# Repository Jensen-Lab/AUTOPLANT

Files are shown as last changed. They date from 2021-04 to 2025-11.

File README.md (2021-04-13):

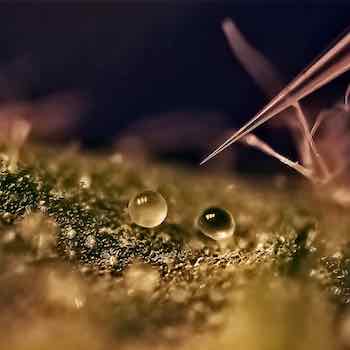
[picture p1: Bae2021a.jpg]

# Supplemental Online Material
Neural networks and robotic microneedles enable autonomous extraction of plant metabolites

Plant Physiology (2021)

Hansol Bae, Magnus Paludan, Jan Knoblauch and Kaare H. Jensen

Department of Physics, Technical University of Denmark, DK-2800 Kgs. Lyngby

E-mail for correspondence: khjensen@fysik.dtu.dk

This repository contains scripts for
1. controlling a Sutter Instruments ROE-200 micromanipulator ("micromanipulator/") 
2. generating training data for a CNN for glandular trichome detection on micrographs ("generate_training_data/") 
3. training (transfer learning) GoogLeNet for glandular trichome detection on micrographs ("train_neural_network/") 
4. testing the network on micrographs ("test_neural_network/") 

To generate training data, train the network, and test the network follow these steps: 
Steps 1-4 may be skipped, as the network is already trained (network weights in train_neural_network/neuralNet.mat). 

Generating training data (MAY BE SKIPPED): 
1. make folder "training_data" in "generate_training_data". 
2. make folders "negative" and "positive" in "generate_training_data/training_data" 
3. run the MATLAB code "generate_training_data/generate_training_data.m"

Training (transfer learning) GoogLeNet CNN (MAY BE SKIPPED): 
4. run the MATLAB code "train_neural_network/train_network.m" 

Test the neural network: 
5. run the MATLAB code test_neural_network/test_network.m 
6. on line 16 the variable "imageNo" may be changed to any image index in "generate_training_data/full_res_images/". Alternatively, a full-path to a micrograph may be inserted in line 17.

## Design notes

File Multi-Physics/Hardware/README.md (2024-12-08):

# Six-Axis Micro Manipulator Assembly Guide

## Overview
This document provides detailed instructions for assembling the Six-Axis Micro Manipulator.

## Hardware Requirements
A list of all required hardware is provided in the file `Parts.xlsx` including links to suppliers for purchase of commercial available parts. 
- Parts marked as 'bought' will have to be purchased.
- Parts marked as '3D Print' will have to be 3D printed. The corresponding `.stl` files can be found in the folder `3DPrints` sorted into the individual axis.
- Parts that are marked as `Workshop` are metal components. Files with dimensions are included in `Metal_Connectors`. These parts will have to be made or ordered.

### Additional Requirements
- Screws (M2, M3, M4 and M6 of adequate lengths)
- Screwdrivers (corresponding to the screws)

## Electronics Required
The wiring digrams (Schematics) for the electronic setup is included in the folder `PCB`.
- Schematic for the motor drivers. If all six axis are in use, this electronis set-up has to be repeated for each individual axis (For ordering a premade PCB: Gerber, BOM and Pick and Place Files are available for a manual control of the motor (see `software`for the difference in manual and automatic control)
- Schematic for the electronic setup of the `electrode` probe.
- Schematic for the electronis setup of the `laser`probe.

### Additional Requirements
- Wire extensions / Connetions
- Breadboards
- (Soldering Iron)

## Assembly Instructions
The `3DPrints/Robot.step` file illustrates how the different parts fit together. Remember to wire the motors according to the elctronic schematics after assembly.

If automatic mode is wished (as of now implemented only for x,y, and r), follow these steps:
- glue the magnet holder to the back of the motor (the free rotating piece)
- add the magnet
- add the sensor board on the shield
- attach the motorscrew spacer and then the sensor shield to the back of the motor (screws of the motor have to be exchanged for longer ones)
- add the wiring

### Step 1: Z-Axis
- The axis is the base. Add the brackets at the desired height and attach the platform.
- The motor is connected via the metal connector and kept in place with the clamp, plate and block.

### Step 2: Rotational-Axis 1
- A base plate for extra height is the base.
- Attach the Stage to this platform in such a way that the connection to the motor will cross over the flat corner.
- Attach the base to the Z-axis.
- Add the motor via the metal connector. It is held in place at the appropiate distance on the Z axis with the printed motor holder

### Step 3: X-Axis and Y-Axis
- For extra height place the height plate in between the rotational 1 axis and the x axis.
- Attach the motors to the motor holders (x and y).
- Attach the moving part of the x stage (bottom) to the y holder
- Attach the x stage to the X-Stage print (on the non movable part)
- Now the printed stages x and y should be just on top of each other.
- Connect the motor holder and the x stage print with the connection piece and connect the motor shaft with the x axis via the metal connection.
- Connect the y stage onto the movable part of the x stage
- Connect the y axis with the motor shaft via the metal connector.
- Connect the stage system to rotation 1.

### Step 4: Rotational Axis 2
- Attach the motor holder to the y stage
- Add the motor to the holder (be careful when exchanhing the screws of the motor for attachment, so the gears do not fall out of the box.

### Step 5: R-Axis
- Add the motor to the holder
- Add the stage to the holder and connect the stage and motor via the metal connector.
- Add the metal rod to the rod holder and attach the piece to the stage
- Attach the stage to the rotatonal axis 2

## Connection with the PC
For setting up the software see the `README.md` file in the `Software` folder

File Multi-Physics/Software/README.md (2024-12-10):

# Six-Axis Micro Manipulator Control

## Overview
This web application provides an interface to control a six-axis movement system integrated with camera functionalities (Basler acA1920-150uc), acquisition settings, and end effector controls. The app allows users to manipulate and monitor their equipment through a web interface.

## Features
- **Six-Axis Movement Control**: Control over all six axis.
- **Camera Integration**: Live camera view to monitor operations.
- **Acquisition Settings**: Customizable settings to adjust the camera acquisition parameters.
- **End Effector Control**: Interface to access the Laser and Electrode probes.

## Requirements
- Compatible with Linux systems.
- Requires Python 3.8 or newer.
- Dependencies are listed in the `requirements.txt` file.
- Requires the six axis micromanipulator as designed here

## Folders
- **Micromanipulator App**: Here the user interface is designed.
- **Stepper Motor Code**: This code should be uploaded to the microcontrollers (`Raspberry Pi Picos`) of the stepper motors. It defines all necessary movement control, use eg `PlatformIO Core` for uploading the code
- **Electrode**: This code should be uploaded to the microcontroller (`Arduino Nano`) of the Electrode to allow for control of the switch, use eg `PlatformIO Core` for uploading the code.
- **Laser**: This code should be uploaded to the microcontroller (`Arduino Nano`) of the Laser to allow for control of the switch, use eg `PlatformIO Core` for uploading the code.

## Installation
To set up the web app on your local system, follow these steps:
1. Clone the repository to your local machine.
2. Navigate to the cloned directory.
3. Install the required Python dependencies:
   ```bash
   pip install -r requirements.txt
4. Inside of `Micromanipulator App/website/view.py` change the following:
   - `path`: change to the path that should be used to save images and videos
   - `SN_dict`: change to the serial numbers of the respective used microcontrollers

## Use
To open the web application, follow these steps:
1. Navigate to the directory containing `main.py` (in `Micromanipulator App/`)
2. run
    ```bash
   python main.py
4. Access the web app through your browser at the specified local address

### Camera
1. Turn on the camera (`Real-Time Display Basler`) -  Make sure the camera is connected via USB
2. Change exposure, gain blacklevel and gamma value accordingly (`Camera Settings`)
3. Change the total time of a video to be taken and the fps value (`Video Acquisition Settings`)
4. Take an image or video

### Axes
- Connect an axis and wait for the green symbol to appear next to the axis name (`Connection`)
- Input the number of steps in `manual` mode in `Robot Control` to move that amount; in `automatic` mode input the positional change
    (Note: in `automatic` mode a magnet is used to control the positioning)
    (Note: The tick box next to some axes in `Robot Control` changes the movement mode from `manual` to `automatic` when ticked)
- Movement the axis with the corresponding arrows (`Robot Control`)
  
### Electrode 
`Electroshocker Settings`
- Change the total on time of the electrode (eg 60s)
- Change the time the electrode is on (eg 1s)
- Change the time the electrode is off (eg 10s)

### Laser
`Laser Settings`
- Change the total on time of the laser (eg 60s)
- Change the time the laser is on (eg 1s)
- Change the time the laser is off (eg 10s)

## Liscence

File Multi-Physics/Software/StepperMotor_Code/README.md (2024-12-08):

How to build PlatformIO based project
=====================================

1. [Install PlatformIO Core](https://docs.platformio.org/page/core.html)
2. Download [development platform with examples](https://github.com/platformio/platform-raspberrypi/archive/develop.zip)
3. Extract ZIP archive
4. Run these commands:

```shell
# Change directory to example
$ cd platform-raspberrypi/examples/arduino-blink

# Build project
$ pio run

# Upload firmware
$ pio run --target upload

# Clean build files
$ pio run --target clean
```

## Notes

For Raspberry Pi Pico devices, two Arduino cores exist:
* https://github.com/arduino/ArduinoCore-mbed
* https://github.com/earlephilhower/arduino-pico

This examples showcases how to use both of these cores in the `platformio.ini`.

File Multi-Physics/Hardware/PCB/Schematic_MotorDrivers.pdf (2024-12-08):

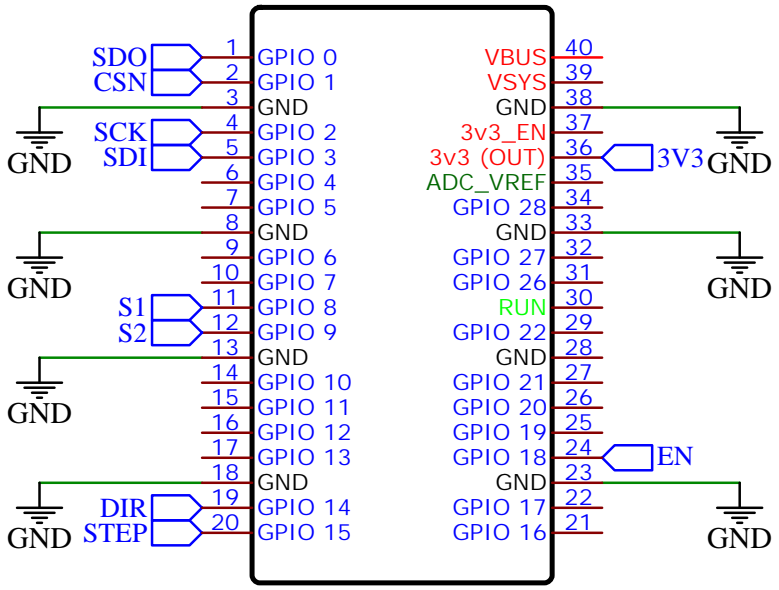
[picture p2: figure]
GND; STEP; DIR; SDI; SCK; CSN; SDO; GPIO 0 1; GPIO 1; GPIO 2; GPIO 3; GPIO 4; GPIO 5; GPIO 6; 9 GPIO 7 10 GPIO 8 11 GPIO 9 12 GND 13 GPIO 10 14 GPIO 11 15 GPIO 12 16 GPIO 13 17 GND 18 GPIO 14 19

GPIO 15 20 | GPIO 16 21 GPIO 17 22 GND 23 GPIO 18 24 GPIO 19 25 GPIO 20 26 GPIO 21 27 GND 28 GPIO 22 29 RUN 30 GPIO 26 31 GPIO 27 32 GND 33 GPIO 28 34 ADC_VREF 35 3v3 (OUT) 36 3v3_EN 37 GND 38 VSYS 39 VBUS 40

## Raspberry Pi Pico

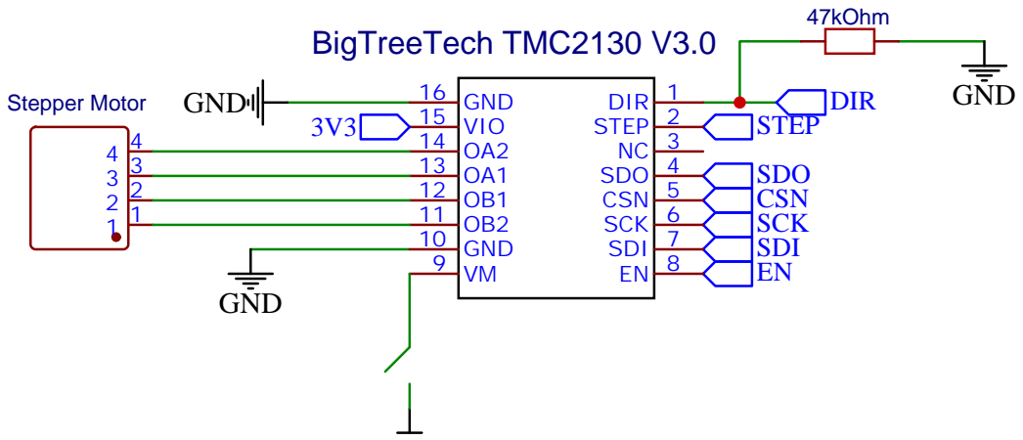
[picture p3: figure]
GND; 47kOhm; DIR; SDI; SCK; CSN; SDO; STEP; BigTreeTech TMC2130 V3.0; Stepper Motor 1 1 2 2 3 3 4 4

GND 10 OB2 11 OB1 12 OA1 13 OA2 14 VIO 15 GND 16

12V

## AS5048B-AB-1.1

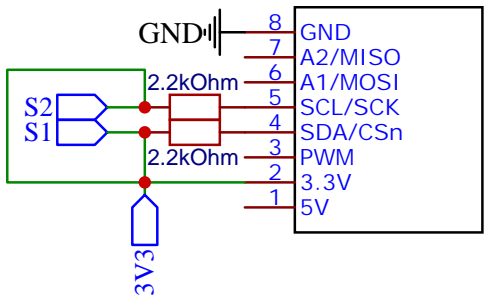
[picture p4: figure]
PWM; SDA/CSn; SCL/SCK; A1/MOSI; A2/MISO; GND; 8 GND; 2.2kOhm

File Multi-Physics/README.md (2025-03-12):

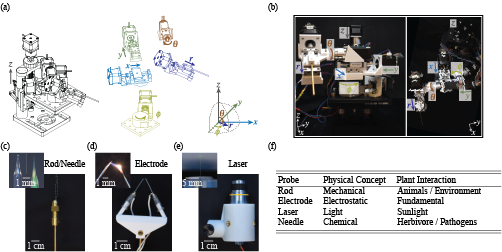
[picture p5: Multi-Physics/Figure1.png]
Key Figure


# Supplemental Material for "A multi-physics approach to probing plant responses: From calcium signaling to thigmonastic motion"

This repository contains supplemental material for the paper titled:

"A multi-physics approach to probing plant responses: From calcium signaling to thigmonastic motion" 
Sabrina Gennis, Matthew D. Biviano, Kristoffer P. Lyngbirk, Hannah R. Thomas, Viktoriya Vasina, Christine Faulkner, Michael Knoblauch and Kaare H. Jensen

Here, you will find additional data, and resources to build and use the six axis micromanipulator and the different probes that are used in the paper.

## Contact Information
**Kaare Jensen**
- Email: khjensen@fysik.dtu.dk
- Institution: Department of Physics, Technical University of Denmark, DK-2800 Kgs. Lyngby

## Contents of This Repository
- `Hardware/`: Description of all the hardware needed for building the system and instructions for setting it up.
- `Software/`: Directory containing the software for the system.

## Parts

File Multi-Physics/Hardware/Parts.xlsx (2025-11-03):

Micromanipulator
Parts and Costs
Movement Axis | Part | 3DPrint | Workshop | Bought | Order Number | Cost | Quantity | Total Cost in EUR | Conversion Rate
X-Axis | Stage |  |  | norelem | 21134-304 (https://www.norelem.com/dk/en/Products/Product-overview/Systems-and-components-for-machine-and-plant-construction/21000-Slides-Guide-rails-Positioning-tables-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) | 275.54 € | 1 | 275.54 € | USD to EUR | 0.89
 | Motor |  |  | makersupplies | MT-1703HSM168A (https://makersupplies.dk/electrical-cnc-electronics/stepper-drivers-motors/hybrid-stepper-motor/stepper-drivers-motors-stepper-motors-hybrid-stepper-motor-mot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) | 212.50 kr. | 1 | 28.48 € | DKK to EUR | 0.134
 | X-axis - MotorHolderNema17 | PLA |  |  |  |  | 1
 | X-axis - Height_Plate | PLA |  |  |  |  | 1
 | X-axis - X_stage_on_rotational_stage | PETG |  |  |  |  | 1
 | X-axis - Connection | PETG |  |  |  |  | 1
 | Stages_Drive connector |  | Metall |  |  |  | 1
 | Megnetic Sensor Board |  |  | RS | 201-8314 (https://dk.rs-online.com/web/p/sensor-udvikling/2018314?searchId=9923297d-1d02-4ba0-9d2d-780a1fe3a02a) | 130.60 kr. | 1 | 17.50 €
 | Motor_sensor_shield | PLA |  |  |  |  | 1
 | Motor-magnet-holder | PLA |  |  |  |  | 1
 | motorscrew-spacer | PLA |  |  |  |  | 1
Y-Axis | Stage |  |  | norelem | 21120-04 (https://www.norelem.com/dk/en/Products/Product-overview/Systems-and-components-for-machine-and-plant-construction/21000-Slides-Guide-rails-Positioning-tables-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) | 241.44 € | 1 | 241.44 €
 | Motor |  |  | makersupplies | MT-1703HSM168A (https://makersupplies.dk/electrical-cnc-electronics/stepper-drivers-motors/hybrid-stepper-motor/stepper-drivers-motors-stepper-motors-hybrid-stepper-motor-mot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) | 212.50 kr. | 1 | 28.48 €
 | Y-axis - Holder | PLA |  |  |  |  | 1
 | Stages_Drive connector |  | Metall |  |  |  | 1
 | Megnetic Sensor Board |  |  | RS | 201-8314 (https://dk.rs-online.com/web/p/sensor-udvikling/2018314?searchId=9923297d-1d02-4ba0-9d2d-780a1fe3a02a) | 130.60 kr. | 1 | 130.60 €
 | Motor_sensor_shield | PLA |  |  |  |  | 1
 | Motor-magnet-holder | PLA |  |  |  |  | 1
 | motorscrew-spacer | PLA |  |  |  |  | 1
Z-Axis | Stage |  |  | thorlabs | VAP4/M (https://www.thorlabs.com/newgrouppage9.cfm?objectgroup_id=9434) | $812.53 | 1 | 723.15 €
 | Motor |  |  | amazon | Stepperonline 27:1 Planetary Gear Nema 17 (https://www.amazon.de/dp/B077YXYTDD?psc=1&ref=ppx_yo2ov_dt_b_product_details) | 45.16 € | 1 | 45.16 €
 | Z-axis_Motor connector |  | Metall |  |  |  | 1
 | Z-axis_Motor clamp | PLA |  |  |  |  | 1
 | Z-axis_Motor plate | PLA |  |  |  |  | 1
 | Z-axis_Mount block | PLA |  |  |  |  | 1
 | Platform |  |  | thorlabs | MB1515/M (https://www.thorlabs.com/thorproduct.cfm?partnumber=MB1515/M) | $57.07 | 1 | 50.79 €
 | Platform Brackets |  |  | thorlabs | AB90A/M (https://www.thorlabs.com/thorproduct.cfm?partnumber=AB90A/M) | $30.58 | 2 | $54.43
Rotational Axis | Stage |  |  | norelem | 21160-08 (https://www.norelem.com/dk/en/Products/Product-overview/Systems-and-components-for-machine-and-plant-construction/21000-Slides-Guide-rails-Positioning-tables-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) | 344.38 € | 1 | 344.38 €
 | Motor |  |  | amazon | Stepperonline 27:1 Planetary Gear Nema 17 (https://www.amazon.de/dp/B077YXYTDD?psc=1&ref=ppx_yo2ov_dt_b_product_details) | 45.16 € | 1 | 45.16 €
 | Rot-axis - MotorHolderNema17 | PETG |  |  |  |  | 1
 | Stages_Drive connector |  | Metall |  |  |  | 1
 | Rot-axis - BasePlate | PLA |  |  |  |  | 1
Rotational 2 Axis | Motor |  |  | amazon | Stepperonline 14:1 Planetary Gear Nema 11 (https://www.amazon.de/-/en/dp/B077Z7WGV6?ref=ppx_yo2ov_dt_b_fed_asin_title) | 212.50 kr. | 1 | 50.00 €
 | Rot2_MotorHolderNema11 | PLA |  |  |  |  | 1
R-axis | Motor |  |  | amazon | Stepperonline Nema 11 Geared Motor 14:1 Planetary Gearbox 0.67A Stepper Motor (https://www.amazon.de/dp/B077Z7WGV6?ref=ppx_yo2ov_dt_b_fed_asin_title) | 114.27 € | 1 | 114.27 €
 | r-axis_holder | PETG |  |  |  |  | 1
 | r-axis_rod_holder | PLA |  |  |  |  | 1
 | Stages_Drive connector |  | Metall |  |  |  | 1
 | Metal Rod (3mm diameter) |  | Metall |  |  |  | 1
 | Megnetic Sensor Board |  |  | RS | 201-8314 (https://dk.rs-online.com/web/p/sensor-udvikling/2018314?searchId=9923297d-1d02-4ba0-9d2d-780a1fe3a02a) | 130.60 kr. | 1 | 17.50 €
 | Motor_sensor_shield | PLA |  |  |  |  | 1
 | Motor-magnet-holder | PLA |  |  |  |  | 1
 | motorscrew-spacer | PLA |  |  |  |  | 1
Power Supply | Power Supply 24V |  |  | amazon | IRM-60-24ST AC/DC 60W (https://www.amazon.de/gp/product/B01H0X8EJI/ref=ppx_yo_dt_b_asin_title_o02_s00?ie=UTF8&psc=1) | 21.00 € | 1 | 21.00 €
 | Power Supply Box |  |  | amazon | ABS Housing 158x90x60 (https://www.amazon.de/gp/product/B0747M7BWZ/ref=ppx_yo_dt_b_asin_title_o01_s02?ie=UTF8&th=1) | 13.23 € | 1 | 13.23 €
 | PCB Power Divider |  |  | JLCPCB | own design | 5.05 € | 1 | 5.05 €
 | Power Divider Box |  |  | amazon | ABS Housing 158x90x60 (https://www.amazon.de/gp/product/B0747M7BWZ/ref=ppx_yo_dt_b_asin_title_o01_s02?ie=UTF8&th=1) | 13.23 € | 1 | 13.23 €
 | Stop Button |  |  | amazon | Emergency Stop Switch 12-220V 3A 1NO 1NC (https://www.amazon.de/gp/product/B07S2VJT9Q/ref=ppx_yo_dt_b_asin_title_o07_s01?ie=UTF8&th=1) | 15.75 € | 1 | 15.75 €
Driver Electronics | Motor Drivers |  |  | amazon | TMC2130 V3.0 SPI 4x (https://www.amazon.de/gp/product/B07RQXZCGX/ref=ppx_yo_dt_b_asin_title_o07_s01?ie=UTF8&psc=1) | 37.80 € | 2 | 75.60 €
 | Raspberry Pi Pico |  |  | digikey | 2648-SC0915CT-ND (https://www.digikey.com/en/products/detail/raspberry-pi/SC0915/13624793) | $4.00 | 6 | 21.36 €
 | PCB Boards Drivers |  |  | JLCPCB | own design | 2.50 € | 6 | 15.00 €
 | Switches |  |  | amazon | Toggle Switch 10x (https://www.amazon.de/gp/product/B083NLCDQG/ref=ppx_yo_dt_b_asin_title_o00_s00?ie=UTF8&th=1) | 9.44 € | 1 | 9.44 €
 | Electronics Box |  |  | RS | 2010206 (https://de.rs-online.com/web/p/universalgehause/2010206?searchId=89035b39-1f88-4bc5-9d30-509afda7214d&gb=s) | 53.53 € | 1 | 53.53 €
Generel | Nuts and Bolts
 | Brass inserts |  |  | amazon | 330 pieces threaded insert nut (https://www.amazon.de/gp/product/B082R28J4T/ref=ppx_yo_dt_b_asin_title_o06_s00?ie=UTF8&psc=1) | 14.70 € | 1 | 14.70 €
 | USBA-Micro Cable |  |  | RS | 2527125 5x (https://de.rs-online.com/web/p/usb-kabel/2527125?searchId=ae20c1eb-bfac-4bae-ba3b-54ca0c1161e8&gb=s) | 10.57 € | 2 | 21.14 €
 | USBA-USBA Cable |  |  | RS | 2513218 5x (https://de.rs-online.com/web/p/usb-kabel/2513218?searchId=9832e634-1913-4e33-acd7-2c80567f8a2b&gb=s) | 9.77 € | 2 | 19.54 €
Camera | Basler Camera |  |  | Basler | Basler acA1920-150uc (https://www.baslerweb.com/en/shop/aca1920-150uc/) | $1000.00 | 1 | 890.00 €
 |  |  |  |  |  |  |  | 3355.45 €
Probes
Rod | Holder | PETG |  | amazon | Mesee 3 Sets 0.5-3mm Brass Drill Chuck (https://www.amazon.com/dp/B08XWWZ41R?smid=A38WK9AYQDX0WE&ref_=chk_typ_imgToDp&th=1) | $7.99 | 1 | 7.11 €
Electrode | holder | PETG
 | electrical recharchable lighter |  |  | coop
 | arduino nano |  |  | RS | 1927586 (https://de.rs-online.com/web/p/arduino/1927586?searchId=250e394d-1db6-4d03-8f04-e056930f3700&gb=s) | 13.03 € | 1 | 13.03 €
 | relay |  |  | amazon | Electrely 6pcs 1 Channel Relay Module, 5V (https://www.amazon.de/dp/B07GRW83FR?ref=ppx_yo2ov_dt_b_fed_asin_title) | 9.44 € | 1 | 12.48 €
Laser | laser pointer green |  |  | amazon | CTRICALVER 1 x 520 nm 5.5-6 V green laser (https://www.amazon.de/gp/product/B08QYNZDD4/ref=ppx_yo_dt_b_asin_title_o03_s01?ie=UTF8&th=1) | 13.23 € | 1 | 13.23 €
 | microscope lens |  |  | amazon | 10x 185 achromatic lens (160/0.17) (https://www.amazon.de/gp/product/B07PPGDVQK/ref=ppx_yo_dt_b_asin_title_o00_s03?ie=UTF8&psc=1) | 18.98 € | 1 | 18.98 €
 | holder | PETG |  |  |  |  |  | 0.00 €
 | arduino nano |  |  | RS | 1927586 (https://de.rs-online.com/web/p/arduino/1927586?searchId=250e394d-1db6-4d03-8f04-e056930f3700&gb=s) | 13.03 € | 1 | 13.03 €
 | relay |  |  | amazon | Electrely 6pcs 1 Channel Relay Module, 5V (https://www.amazon.de/dp/B07GRW83FR?ref=ppx_yo2ov_dt_b_fed_asin_title) | 9.44 € | 1 | 12.48 €
 |  |  |  |  |  |  |  | 90.34 €

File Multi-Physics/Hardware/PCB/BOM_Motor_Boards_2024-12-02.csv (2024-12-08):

ID | Name | Designator | Footprint | Quantity | Manufacturer Part | Manufacturer | Supplier | Supplier Part | Price
1 | WJ126V-5.0-2P | P2 | CONN-TH_WJ126V-5.0-2P | 1 | WJ126V-5.0-2P | KANGNEX(康奈克斯电气) | LCSC | C8404 | 0.068
2 | X5511FV-20-C30D97-0970 | U3,U4 | HDR-TH_20P-P2.54-V-F-4 | 2 | X5511FV-20-C30D97-0970 | XKB Connectivity(中国星坤) | LCSC | C2883486 | 0.707
3 | 912-112A1027D10100 | USB2 | USB-A-TH_912-112A1027D10100 | 1 | 912-112A1027D10100 | 精拓金 | LCSC | C2763281 | 0.129
4 | 47kΩ | R1 | R0402 | 1 | ERA2AEB473X | PANASONIC(松下) | LCSC | C543615 | 0.12
5 | XH-4AW M | CN1 | CONN-TH_XH2.54-4AW | 1 | - | Boom Precision Elec | LCSC | C146115 | 0.021
6 | X6511FV-08-C85D32 | H3,H4 | HDR-TH_8P-P2.54-V-F | 2 | X6511FV-08-C85D32 | XKB Connectivity(中国星坤) | LCSC | C718237 | 0.192

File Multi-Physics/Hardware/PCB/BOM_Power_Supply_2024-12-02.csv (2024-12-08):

ID | Name | Designator | Footprint | Quantity | Manufacturer Part | Manufacturer | Supplier | Supplier Part | Price
1 | WJ126V-5.0-2P | P2,P1 | CONN-TH_WJ126V-5.0-2P | 2 | WJ126V-5.0-2P | KANGNEX(康奈克斯电气) | LCSC | C8404 | 0.068
2 | 100uF | C1 | CAP-SMD_BD6.3-L6.6-W6.6-LS7.3-FD | 1 | GVZ1H101M0607 | HONOR(荣誉) | LCSC | C2980173 | 0.067
3 | 1N4007_C211605 | D1 | DO-41_BD2.4-L4.7-P8.70-D0.9-FD | 1 | 1N4007 | YANGJIE(扬杰) | LCSC | C211605 | 0.034
4 | 912-112A1027D10100 | USB1,USB2,USB3,USB4,USB5,USB6 | USB-A-TH_912-112A1027D10100 | 6 | 912-112A1027D10100 | 精拓金 | LCSC | C2763281 | 0.129
5 | 220kΩ | R3 | RES-TH_BD2.3-L6.5-P10.50-D0.5 | 1 | RI40-1/4W-220KΩ ±1% T | CCO(千志电子) | LCSC | C136543 | 0.064

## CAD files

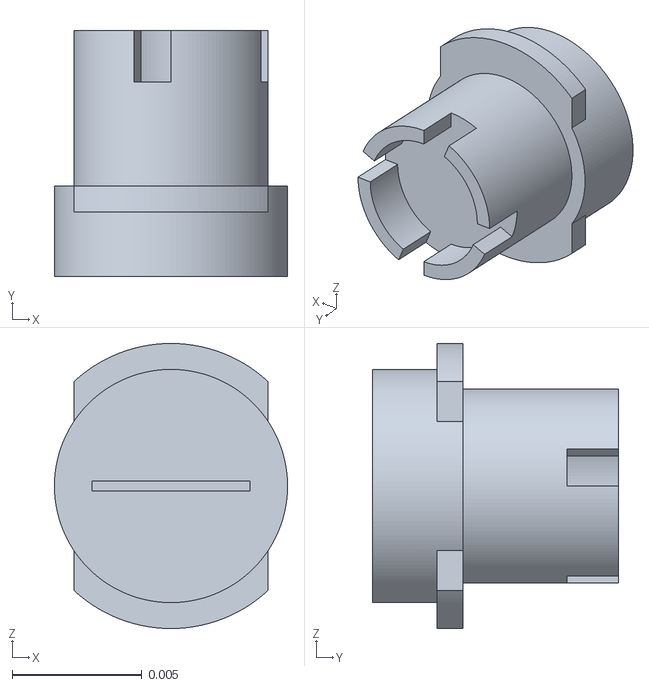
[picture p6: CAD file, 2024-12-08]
Multi-Physics/Hardware/3DPrints/Position_Sensor/Motor-magnet-holder.stl
0.009 x 0.0095 x 0.011

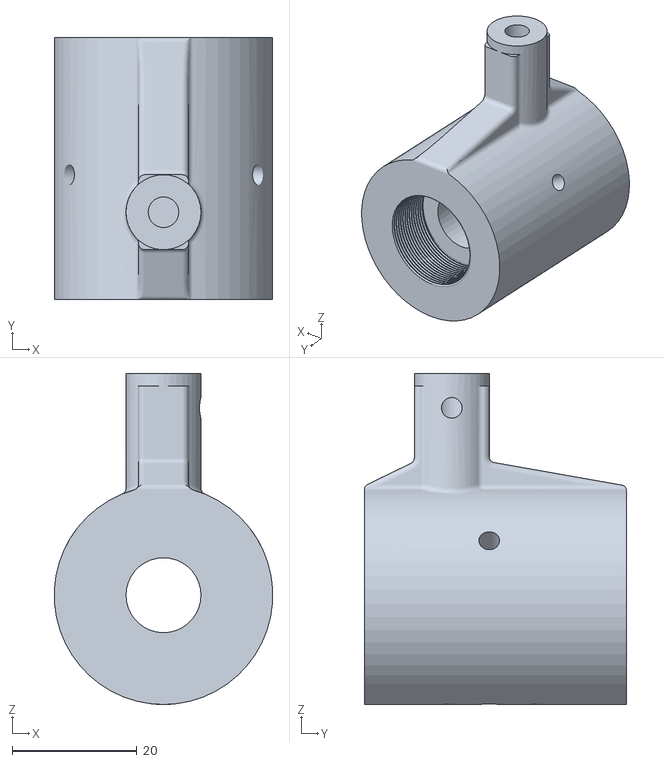
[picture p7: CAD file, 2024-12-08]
Multi-Physics/Hardware/3DPrints/Probes/Laser_Holder.stl
35.0 x 42.0 x 53.0

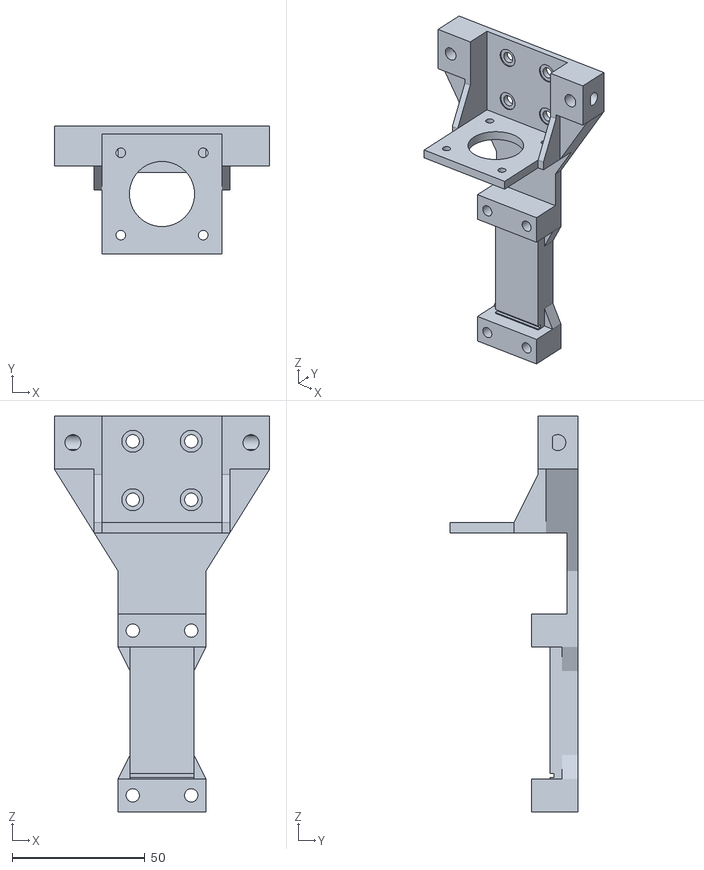
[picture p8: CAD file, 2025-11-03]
Multi-Physics/Hardware/3DPrints/r-axis/r-axis_holder.stl
81.0 x 48.0 x 149.0

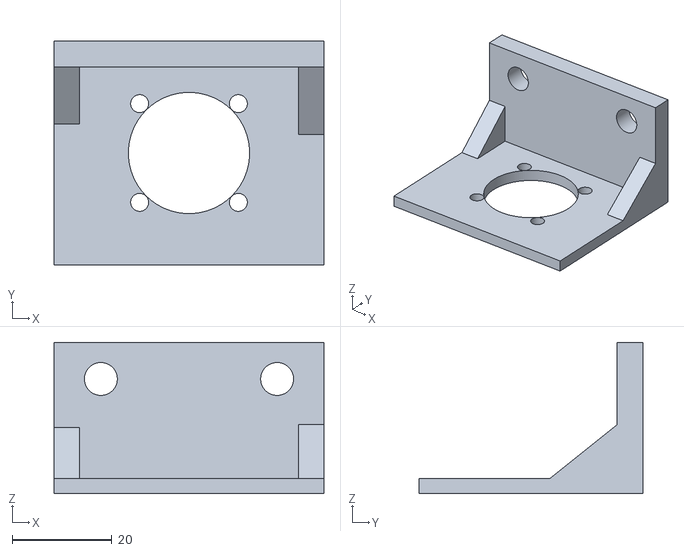
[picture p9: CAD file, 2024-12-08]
Multi-Physics/Hardware/3DPrints/Rot1-axis/Rot-axis - MotorHolderNema17.stl
54.2 x 45.0 x 30.3

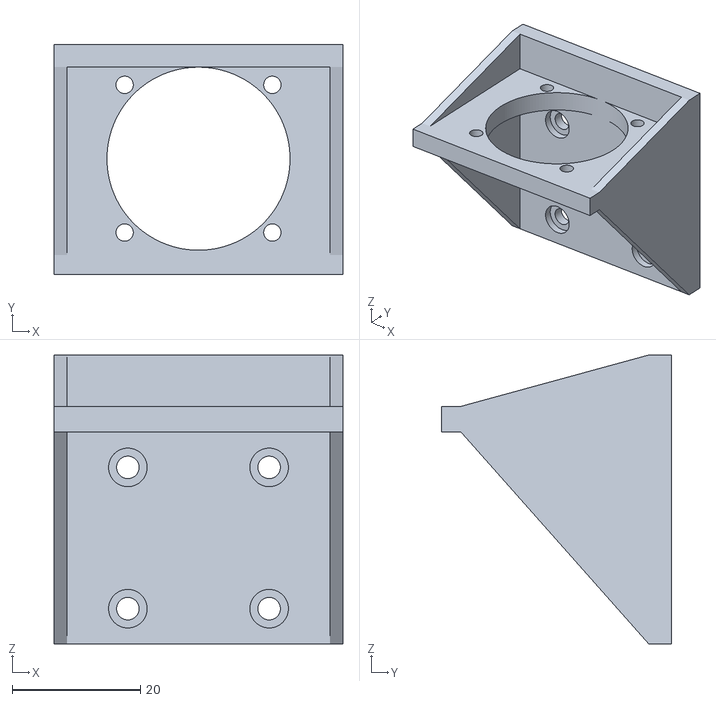
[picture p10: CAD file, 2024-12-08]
Multi-Physics/Hardware/3DPrints/Rot2-axis/Rot2_MotorHolderNema11.stl
45.0 x 35.8 x 45.0

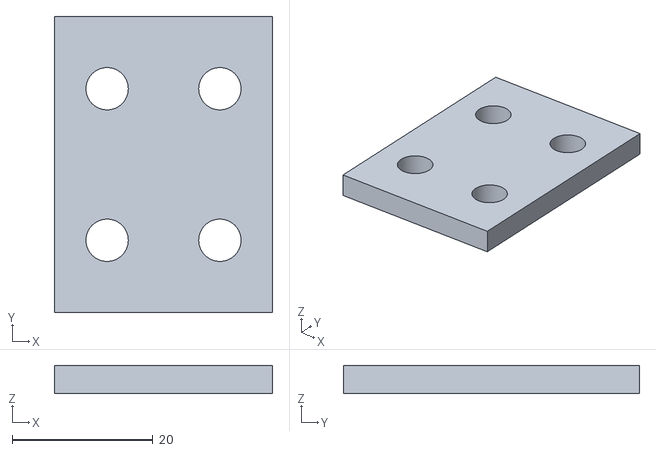
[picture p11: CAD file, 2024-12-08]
Multi-Physics/Hardware/3DPrints/X-axis/X-axis - Connection.stl
31.0 x 42.0 x 4.00

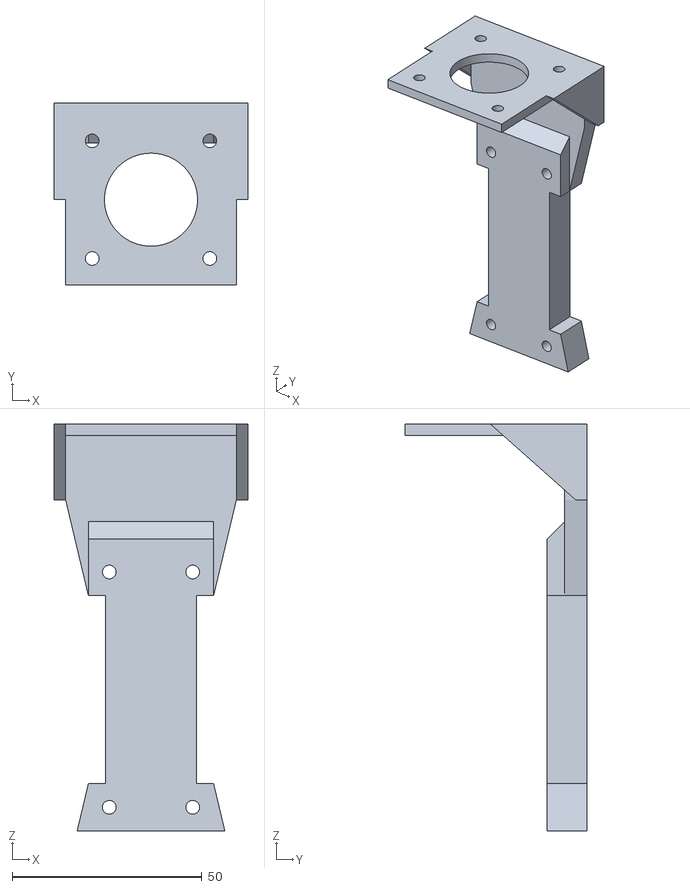
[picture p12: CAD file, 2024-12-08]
Multi-Physics/Hardware/3DPrints/Y-axis/Y-axis - Holder.stl
51.0 x 48.0 x 107.2

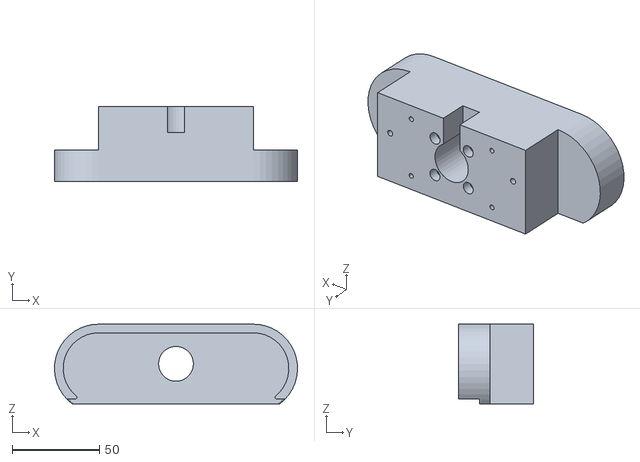
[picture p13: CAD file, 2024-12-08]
Multi-Physics/Hardware/3DPrints/Z-axis/Z-axis_Mount block.STL
139.5 x 43.2 x 45.8

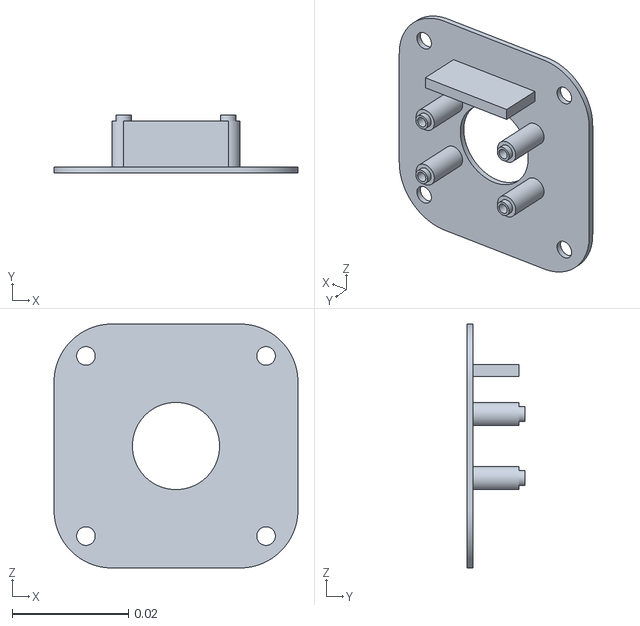
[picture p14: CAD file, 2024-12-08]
Multi-Physics/Hardware/3DPrints/Position_Sensor/Motor_sensor_shield.stl
0.042 x 0.01 x 0.042

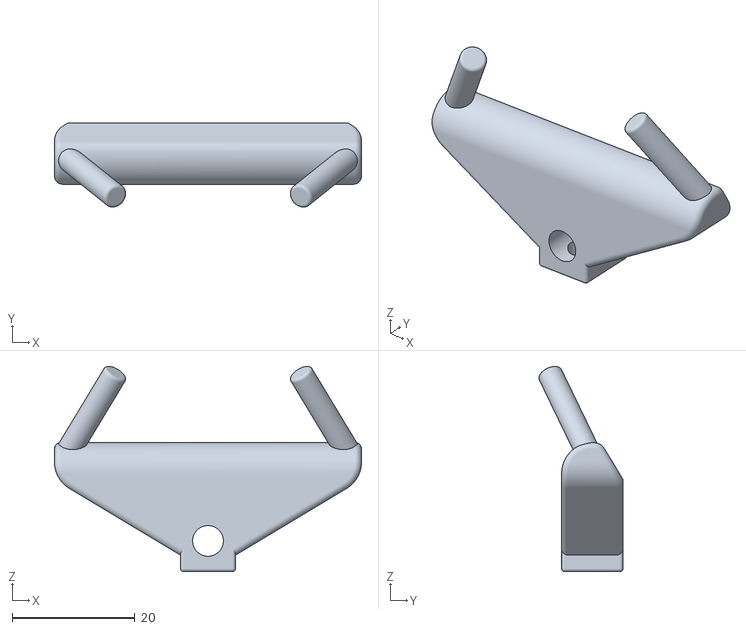
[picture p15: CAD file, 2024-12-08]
Multi-Physics/Hardware/3DPrints/Probes/Electrode_Holder.stl
50.0 x 13.7 x 33.4

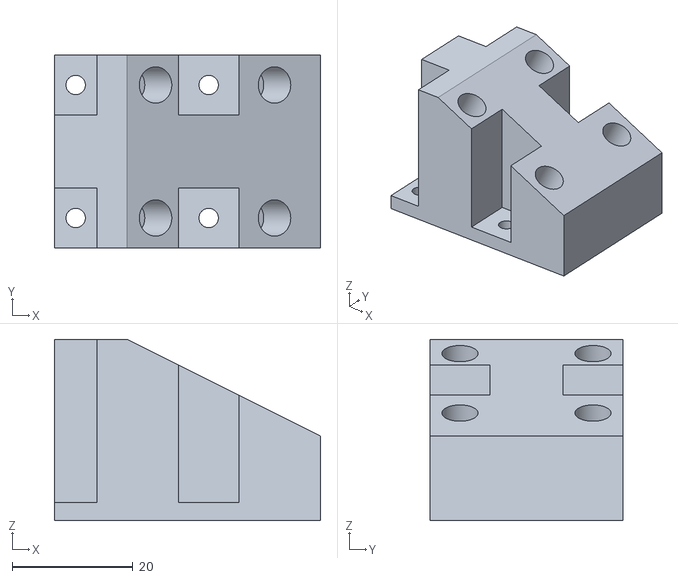
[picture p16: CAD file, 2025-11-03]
Multi-Physics/Hardware/3DPrints/r-axis/r-axis_AnglePlate.stl
44.0 x 32.0 x 30.0

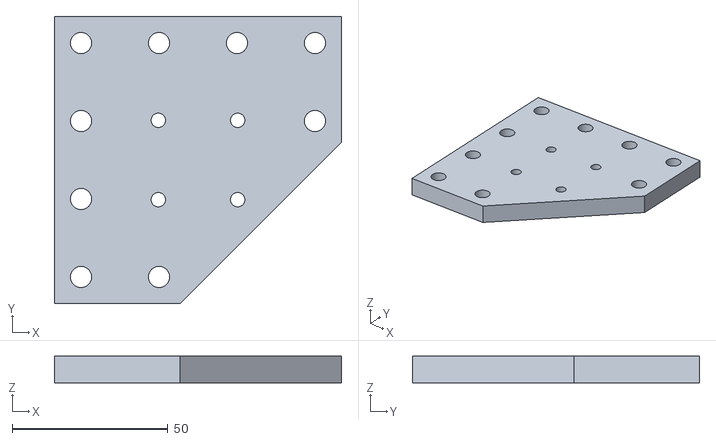
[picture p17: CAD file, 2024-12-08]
Multi-Physics/Hardware/3DPrints/Rot1-axis/Rot-axis - BasePlate.stl
92.0 x 92.0 x 8.51

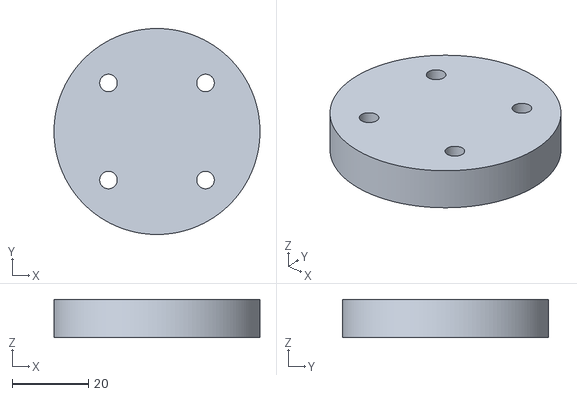
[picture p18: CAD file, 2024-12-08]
Multi-Physics/Hardware/3DPrints/X-axis/X-axis - Height_Plate.stl
54.0 x 54.0 x 10.0

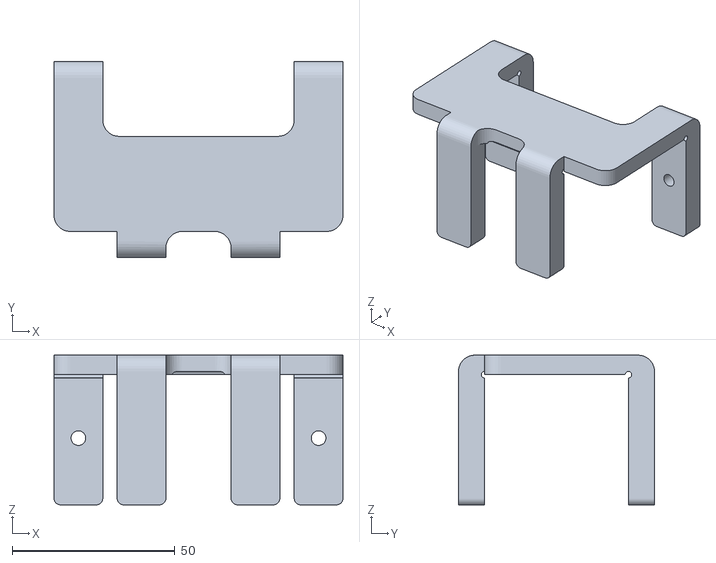
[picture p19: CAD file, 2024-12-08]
Multi-Physics/Hardware/3DPrints/Z-axis/Z-axis_Motor clamp.STL
88.8 x 60.2 x 46.0

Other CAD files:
Multi-Physics/Hardware/3DPrints/r-axis/r-axis_rod_holder.stl
Multi-Physics/Hardware/3DPrints/X-axis/X-axis - MotorHolderNema17.stl
Multi-Physics/Hardware/3DPrints/Z-axis/Z-axis_Motor plate.STL
Multi-Physics/Hardware/3DPrints/X-axis/X-axis - X_stage_on_rotational_stage.stl
Multi-Physics/Hardware/3DPrints/Position_Sensor/motorscrew-spacer.stl

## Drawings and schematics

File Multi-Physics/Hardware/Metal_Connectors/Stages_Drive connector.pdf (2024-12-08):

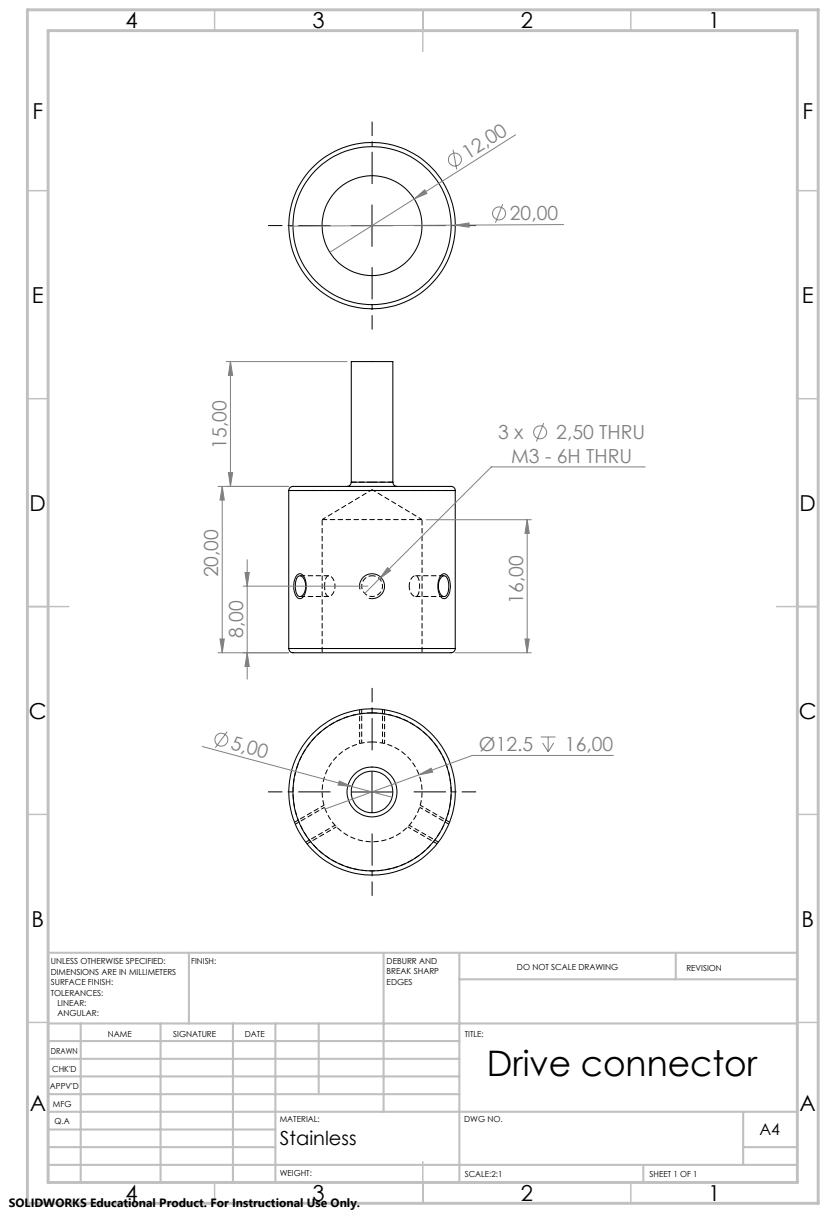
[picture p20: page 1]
2,50 THRU; M3 - 6H THRU 16,00; FINISH:; DEBURR AND; BREAK SHARP; DO NOT SCALE DRAWING; REVISION; SCALE:2:1; SHEET 1 OF 1

UNLESS OTHERWISE SPECIFIED:
DIMENSIONS ARE IN MILLIMETERS
SURFACE FINISH:
TOLERANCES:
LINEAR:
ANGULAR:

NAME | SIGNATURE | DATE | | | | TITLE: Drive connector

DRAWN
CHK'D
APPV'D
MFG
Q.A | | | | MATERIAL: Stainless | DWG NO. | A4

SOLIDWORKS Educational Product. For Instructional Use Only.

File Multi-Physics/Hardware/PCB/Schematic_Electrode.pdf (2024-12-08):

## ARDUINO_NANO Relay

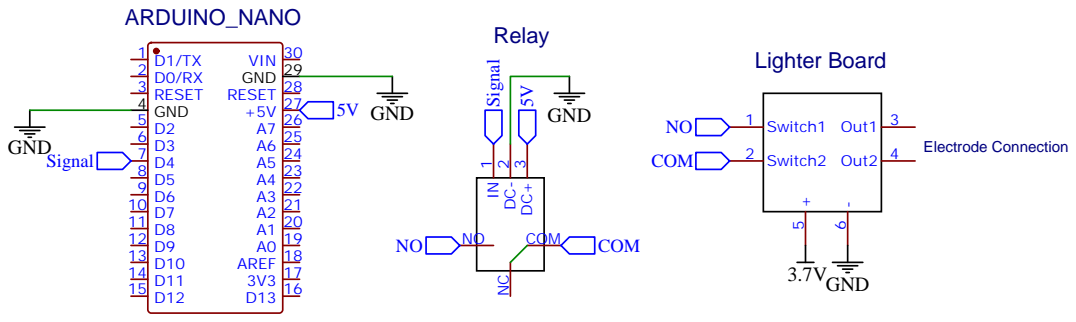
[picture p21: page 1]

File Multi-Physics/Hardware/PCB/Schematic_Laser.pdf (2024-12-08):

## ARDUINO_NANO Relay

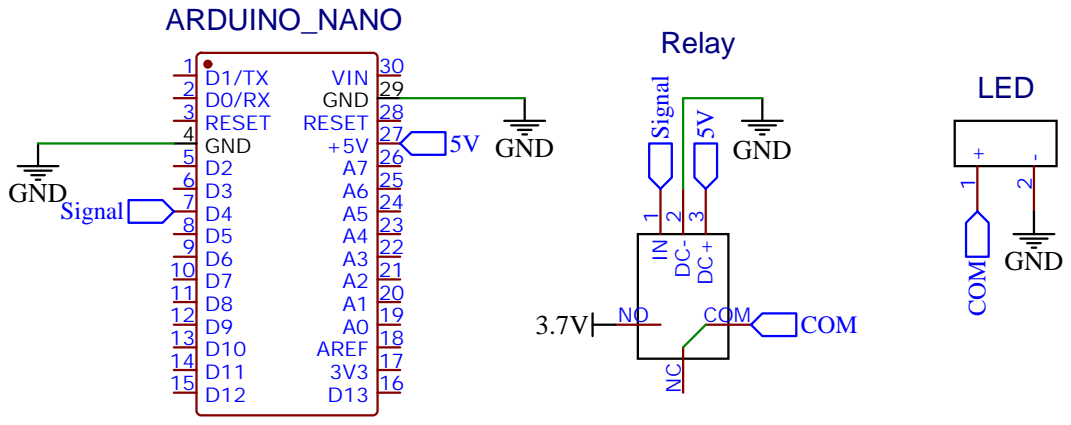
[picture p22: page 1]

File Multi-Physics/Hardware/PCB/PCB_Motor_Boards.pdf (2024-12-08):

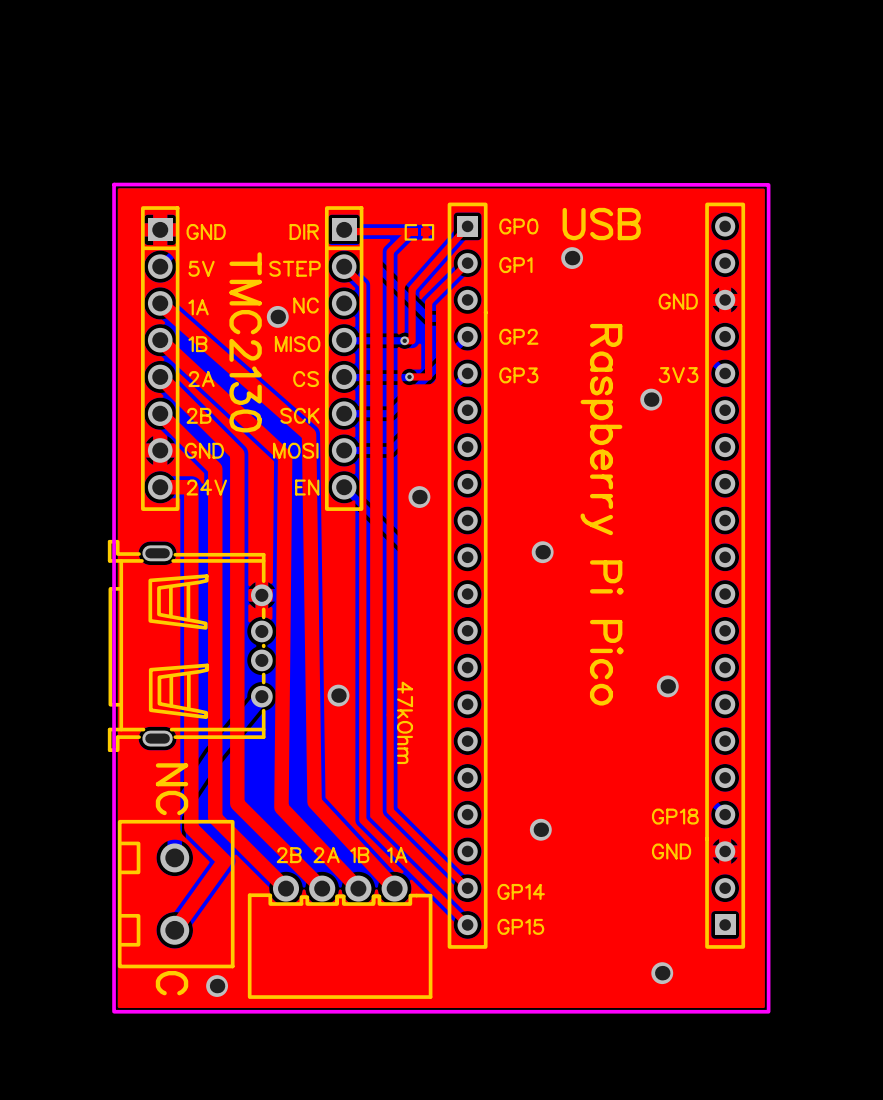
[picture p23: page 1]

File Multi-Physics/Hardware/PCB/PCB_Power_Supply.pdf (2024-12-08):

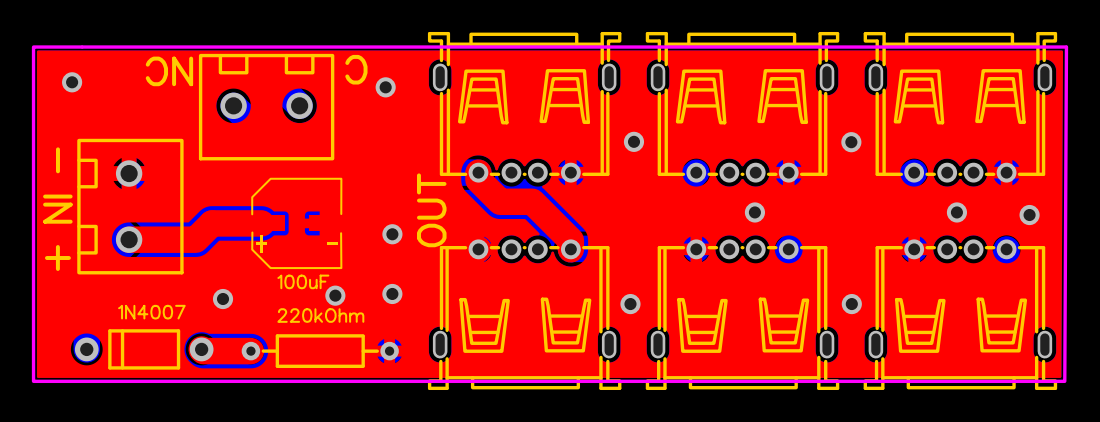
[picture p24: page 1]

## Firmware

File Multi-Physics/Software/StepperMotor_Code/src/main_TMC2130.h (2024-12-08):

/** motor driver TMC2130
  * Raspberry Pi Pico - stepper motor driver support

  * The defaults assumes a TMC2130 stepper driver has been wired up to the Pico as follows:

  *   GND   -> any Pico GND
  *   3V    -> 3V3_EN
  *   DIR   -> GP14
  *   STEP  -> GP15
  *   MISO  -> GP0
  *   CS    -> GP1
  *   SCK   -> GP2
  *   MOSI  -> GP3

  * remember to include a resistor (about 3.3kOhm) between the readout DIR Pin and any GND
  * remember to have the GND on minus (black cable) and Power supply on + (white cable)
*/

// define PINs
// Raspberry Pi Pico:
#define EN_PIN    18   //enable
#define DIR_PIN   14   //direction
#define STEP_PIN  15   //step
#define SW_MISO   0    //Master In Slave Out (MISO)
#define CS_PIN    1    //chip select
#define SW_SCK    2    //Slave Clock (SCK)
#define SW_MOSI   3    //Master Out Slave In (MOSI)

#define R_SENSE     0.11f   // depends on the motor driver

#define STALL_PIN 22 // diag pin

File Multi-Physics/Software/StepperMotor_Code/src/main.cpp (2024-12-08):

#include <Arduino.h>
#include <SPI.h>
#include <Wire.h>
#include <Adafruit_I2CDevice.h>
#include <stdio.h>
#include "pico/stdlib.h"
#include "pico/multicore.h"
#include "hardware/irq.h"
#include "hardware/adc.h"
#include "hardware/sync.h"
#include "hardware/irq.h" // Include the header file that defines SIO_IRQ_PROC0_FIFO
#include <TMCStepper.h>
#include <main_TMC2130.h>
#include <AS5048B_TMC_stepper.h>


#define I2C_ADDRESS 0b1000000
TwoWire wire = TwoWire(i2c0, 8, 9);


Adafruit_I2CDevice i2c_dev = Adafruit_I2CDevice(I2C_ADDRESS, &wire);


TMC2130Stepper driver(CS_PIN, SW_MOSI, SW_MISO, SW_SCK);
AS5048B_TMC_stepper motor = AS5048B_TMC_stepper(i2c_dev, driver);


/// multicore
struct SensorData {
    double value;
};

volatile SensorData sensorData;
volatile bool dataReady = false;


int Nsteps = 0;
int dir = 0;
int dir_old = 0;
int microstep = 0;
int rms_current = 0;
int hold = 0;
int stepDelay = 0;
int autoModeFlag = 0;
double target_position = 0;


void setup(){
  //sleep_ms(1000); // Sleep for 1 second
    Serial.begin(115200); // Start the serial communication
    motor.init();
  //sleep_ms(1000);
}

void loop(){
  //sleep_ms(100); // Sleep for 1 second
  // check for serial input from computer
  sleep_ms(1);

  if (autoModeFlag)
  {
      
    motor.moveTowardsTarget();

    if(Serial.available()>0){
      char readVal = Serial.read();
      if (readVal == 'p'){
        Serial.println(motor.GetCurrentPosition());
      }
      if (readVal == 't'){
        motor.setMaxTolorance(Serial.parseInt());
      }
      if (readVal == 'b'){
        target_position = Serial.parseInt();
        motor.setTargetPosition(target_position);
        Serial.println(target_position);
      }
      if (readVal == 'x'){
        target_position = motor.getTargetPosition() + Serial.parseInt();
        motor.setTargetPosition(target_position);
        Serial.println(target_position);
      }
      if (readVal == 'a'){
        autoModeFlag = Serial.parseInt();
        if (autoModeFlag == 0)
        {
          Serial.println("Mode set to manual");
        }
      }
      if (readVal == 's'){
        autoModeFlag = 0;
        Serial.println("Emergency stop");
        Serial.println("Mode set to manual");
      }
    }
  } else {

    if(Serial.available()>0){
      char readVal = Serial.read();
      if (readVal == 'h'){
          //homed = false;
          // home();
      }
      if (readVal == 'x'){
        Nsteps = Serial.parseInt();
        //steps(dir,Nsteps,max_steps,160,hold,dir_old);
        Serial.println("Move in progress");
        while(Nsteps > 0){
          Nsteps = motor.moveStepsManual(Nsteps, 0,100);

          if(Serial.available()>0){
            char readVal = Serial.read();
            if (readVal == 's'){
              Serial.println("Emergency stop");
              break;
            }
          }
        }  
      }
      if (readVal == 'd'){
        dir_old = dir;
        dir = Serial.parseInt();
        motor.setDirManual(dir);
      }
      if (readVal == 'm'){
        microstep = Serial.parseInt();
        motor.setMicroStepSizeManual(microstep);
      }
      if (readVal == 'r'){
        rms_current = Serial.parseInt();
        motor.setRMSCurrentManual(rms_current);
      }
      if (readVal == 'e'){
        hold = Serial.parseInt();
        motor.setHoldManual(hold);
      }
      if (readVal == 't'){
        stepDelay = Serial.parseInt();
        motor.setStepDelayManual(stepDelay);
      }
      if (readVal == 'p'){
        Serial.println(motor.GetCurrentPosition());
      }
      if (readVal == 'a'){
        autoModeFlag = Serial.parseInt();
        if (autoModeFlag > 0)
        {
          motor.setTargetPosition(motor.GetCurrentPosition());
          Serial.println("Mode set to autonomus");
          Serial.println(motor.getTargetPosition());
        }
      }
    }
  }
}


void setup1() {
   // while (!motor.init_flag)
   // {
        
   // }
    sleep_ms(1000); // Sleep for 1 second
}


void loop1() {

  sleep_ms(1);
  motor.positionAvgFilter(0.05);
    //motor.getTotalPosition();
    //motor.getCurrentAngle



}

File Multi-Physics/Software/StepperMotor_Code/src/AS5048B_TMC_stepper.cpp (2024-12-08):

#include <AS5048B_TMC_stepper.h>
#include <SPI.h>
#include <TMCStepper.h>
#include <Adafruit_I2CDevice.h>
#include <main_TMC2130.h>
#include <cmath>



    AS5048B_TMC_stepper::AS5048B_TMC_stepper(Adafruit_I2CDevice& dev, TMC2130Stepper& stepper)
        : i2c_dev(dev), driver(stepper) {

        encoderValuesAdress = 0XFA+4;
        encoderResolution = 16384;
        tolorance = 0.25;
        IIRVal = 0.80;

        current_position = 0;
       

        AvgPos = 0;
        

        target_position = 0;
        position_error = 0;

        rotations = 0;
        angle_value = 0;
        angle_value_old = 0;
        
        pos_hysterese_flag = true;
        neg_hysterese_flag = true;


        stepCounter = 0;
        dir = 0;
        dir_old = 0;
        steps = 10000;
        stepDelay = 200;
        microstep = 16;
        rms_current = 950;
        hold = 1;
        homed = false;
        max_steps = 1000;  
        max_stepsManual = 100000;

        

        bool init_flag = false;

        }


    void AS5048B_TMC_stepper::init(){
        pinMode(EN_PIN, OUTPUT);
        pinMode(STEP_PIN, OUTPUT);
        pinMode(DIR_PIN, OUTPUT);
        pinMode(CS_PIN, OUTPUT);
        pinMode(STALL_PIN, INPUT_PULLUP);

        SPI.begin(); // Begin SPI communication
        driver.begin();
        driver.rms_current(rms_current); // Set motor RMS current
        
        driver.microsteps(microstep);   // Set microsteps
        driver.en_pwm_mode(true);

        // driver.diag1_stall(true);   // for x and y stallguard
        // driver.diag1_stall(false);  // disable stallguard
        driver.TPWMTHRS(10);           // disable stallguard
        driver.pwm_ampl(255);          // disable stallguard

        driver.TCOOLTHRS(0xFFFFF); // Maximum coolstep threshold
        driver.semin(5);
        driver.semax(2);
        driver.sedn(0b01);
        // driver.sgt(6);              // for x and y stallguard 

        digitalWrite(STEP_PIN,HIGH);
        delayMicroseconds(100);
        digitalWrite(STEP_PIN,LOW);
        delayMicroseconds(100);
        digitalWrite(EN_PIN, LOW);     //hold motor position

        i2c_dev.begin();
        i2c_dev.setSpeed(400000); // Set the I2C clock to 400kHz
        sleep_ms(100); // Sleep for 100ms

        for (size_t i = 0; i < 10; i++)
        {
            sleep_ms(100);
            getCurrentAngle();
        }
        
        sleep_ms(100);
        double angle_value_old = getCurrentAngle();

        if (angle_value_old > encoder_res/2)
        {
            rotations = -1;
        } else
        {
            rotations = 0;
        }
        

        
        //for (size_t i = 0; i < 100; i++)
        // first_pos = positionAvgFilter(0.2);
        
        
        AvgPos = angle_value_old;
        target_position = getTotalPosition();
        init_flag = true;
        
    }


    int AS5048B_TMC_stepper::getMicroStepSize(){
        return microstep;
    }
    void AS5048B_TMC_stepper::setMicroStepSizeManual(int microstep){
        this->microstep = microstep;
        driver.microsteps(microstep);
    }

    int AS5048B_TMC_stepper::getRMSCurrent(){
        return rms_current;
    }
    void AS5048B_TMC_stepper::setRMSCurrentManual(int current){
        this->rms_current = current;
        driver.rms_current(current);
    }

    int AS5048B_TMC_stepper::getHold(){
        return hold;
    }
    void AS5048B_TMC_stepper::setHoldManual(bool hold){
        this->hold = hold;
    }

    int AS5048B_TMC_stepper::getStepDelay(){
        return stepDelay;
    }
    void AS5048B_TMC_stepper::setStepDelayManual(int delay){
        this->stepDelay = delay;
    }



    void AS5048B_TMC_stepper::setMaxTolorance(double tolorance){
        this->tolorance = tolorance;
    }

    double AS5048B_TMC_stepper::getTargetPosition(){
        return target_position;
    }

    int AS5048B_TMC_stepper::getDir(){
        return dir;
    }
    void AS5048B_TMC_stepper::setDirManual(int dir){
        this->dir = dir;
        driver.shaft(dir);
    }

    void AS5048B_TMC_stepper::setTargetPosition(double target){
        target_position = target;
    }

    double AS5048B_TMC_stepper::positionAvgFilter(double IRR) {
    // Implementation of the position average filter

        AvgPos = AvgPos* (1-IRR)+ getTotalPosition() * IRR;
    
        //while(!rp2040.fifo.available())
        
        //rp2040.fifo.pop();
        //angle_mutex.lock();
        current_position = AvgPos;
        //angle_mutex.unlock();
        //rp2040.fifo.push(1);
        

    return AvgPos; // Placeholder return
    }


    double AS5048B_TMC_stepper::GetCurrentPosition(){
        double temp_current_position = 0;

        //int command = 1;
        //rp2040.fifo.push(command);

        //while(!rp2040.fifo.available())
        rp2040.fifo.idleOtherCore();
        temp_current_position = current_position;
        rp2040.fifo.resumeOtherCore();
        //rp2040.fifo.pop();
        

        return temp_current_position;
    }

    double AS5048B_TMC_stepper::getCurrentAngle() {
    double current_angle = 0;
    uint8_t data[2];
    i2c_dev.write_then_read(&encoderValuesAdress, 1, data, 2,false); 
    current_angle = (uint16_t)data[0]<<6 ;
    current_angle += (uint16_t)data[1] & 0b111111;
    return current_angle;
    
    }

    double AS5048B_TMC_stepper::getTotalPosition() {
        

      angle_value = getCurrentAngle();

    //   if (angle_value_old > highHys && angle_value < lowHys && pos_hysterese_flag == true) // If the angle goes over 0 point from high to low and the positive hysteresis flag is set
    //  {
    //     rotations++; // Increment the rotations
    //     pos_hysterese_flag = false; // Reset the hysteresis flag
    //     neg_hysterese_flag = true; // Set the hysteresis flag for the other direction
    //   } else if (angle_value_old < lowHys && angle_value > highHys && neg_hysterese_flag == true) // If the angle goes over 0 point from low to high and the negative hysteresis flag is set
    //   {
    //     rotations--; // Decrement the rotations
    //     pos_hysterese_flag = true; // Set the hysteresis flag for the other direction
    //     neg_hysterese_flag = false; // Reset the hysteresis flag
    //   } else if (angle_value_old > highHys && angle_value < highHys) // If the angle crosses the high hysteresis range
    //   {
    //     neg_hysterese_flag = true; // Set the hysteresis flag to allow negative rotation incrementation
    //   } else if (angle_value_old < lowHys && angle_value > lowHys) // If the angle crosses the low hysteresis range
    //   {
    //     pos_hysterese_flag = true; // Set the hysteresis flag to allow positive rotation incrementation
    //   }

      if (angle_value_old > highHys && angle_value < lowHys) {
        // If the angle goes over 0 point from high to low
        rotations++; // Increment the rotations 
      } else if (angle_value_old < lowHys && angle_value > highHys) {
        // If the angle goes over 0 point from low to high
        rotations--; // Decrement the rotations
      }
      
      angle_value_old = angle_value;

      if (rotations < 0) // If the rotations are negative
      {
        
        return  angle_value - encoder_res + (rotations+1)*encoder_res;
      } else
      {
         // Calculate the current position
         return  angle_value + rotations*encoder_res; // Calculate the current position
      }
        
    //return current_position; // Placeholder return
    }


    double AS5048B_TMC_stepper::moveTowardsTarget(){
        //double test = 0;
        int step_diff = 0;
        int steps_to_move = 0;


        double temp_current_position = 0;

        //int command = 1;
        //rp2040.fifo.push(command);

        //while(!rp2040.fifo.available())

        temp_current_position = GetCurrentPosition();
        //rp2040.fifo.pop();
        

        position_error = (target_position - temp_current_position);
        //Serial.println(temp_current_position);

        if ( abs(position_error) > tolorance){
            //test = position_error;
            if (position_error > 0)
            {
                dir_old = dir;
                dir = 0;
                driver.shaft(dir);  
            }
            else if (position_error < 0)
            {   
                
                dir_old = dir;
                dir = 1;
                driver.shaft(dir);
            }
            microstep = 16;
            step_diff = abs(position_error)/(encoder_res/(400*microstep));
            
            if(step_diff<200){         // for all axis
        
                stepDelay = 5000;       // for all axis
                //Serial.println("slow");
                //driver.rms_current(950);
                steps_to_move = step_diff;
                microstep = 32;

                if (steps_to_move > 10){
                steps_to_move = 10;
                }
            

            } else if(step_diff<1000){         // for all axis
        
                stepDelay = 1000;       // for all axis
                //Serial.println("slow");
                //driver.rms_current(950);
                steps_to_move = (step_diff-190)*0.7;

            }
            else
            {
                stepDelay = 200;
                //Serial.println("fast");
                //driver.rms_current(850);
            
                steps_to_move = (step_diff-950)*0.7;
                
            }
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
